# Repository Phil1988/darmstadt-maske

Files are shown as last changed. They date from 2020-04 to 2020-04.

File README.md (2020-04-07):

# Darmstadt-Maske: Gesichtsmasken für hub-rheinmain und hub-darmstadt

Warum denn "noch eine Maske"? 

Gute Frage - wir haben nach etlichen Erfahrungswerten festgestellt, dass die Prusa-Masken zwar sinnvoll sind und sich zurecht als das Maß für die Masken etabliert hat, aber einige Interessenten fragten nach einer größeren Entfernung zwischen Gesicht und Visier oder der Möglichkeit auch andere, besser desinfizierbare, Kopfbänder zu befestigen.
Außerdem wurde bei unserem Modell die Druckzeit durch Konstruktive veränderungen deutlich reduziert (bis zu 40% schneller).
Dieses Modell ist jedoch weiterhin vollständig kompatibel zur Prusa-Variante, da die Visiere/Schilder identisch sind.

Als groben Richtwert, kann man das Kopfteil in etwa 60min drucken - mit einer 0.4mm Düse.
Wer deutlich länger benötigt, sollte sich nochmal alle Informationen, die wir hier zusammentragen, anschauen oder mit uns in Kontakt treten.

## Qualität und Nachbearbeitung

Wir freuen uns über jeden der der sich uns anschließt und wir gemeinsam noch besser helfen können.
Bitte denkt daran, dass man mit der Herstellung dieser Maske eine gewisse Verantwortung hat.
Daher überprüft bitte selbst die Qualität eurer Drucke.

Hier ein Video das zeigt, welche mechanischer Belastung die Maske aushält:
[Youtube-Video](https://youtu.be/hdetuEkw_Qs )

Das sollte das Modell, dass ihr uns abgebt, auch schaffen.
Masken die schnell kaputt gehen, helfen den Hilfskräften nicht.
Auch täuscht das über unseren wirklich verwendbaren Lagerbestand hinweg.

Druckt das Modell mit mindestens 1mm Wandstärke (also für 0,4mm Düsen mit mindestens 3 Wänden).
Nehmt 30% Füllung/Infill als Gitternetz/Grid oder Gyroid.

Brim (und Pad) sollte auch entfernt worden sein, falls man damit druckt.
Falls man gestapelte (stack) Modelle druckt, sollten diese getrennt abgegeben werden.
Die Innenseite des Kopfteils (welche die Stirn berührt) und die Vorderseite (an die die Folie dran kommt) sollten glatt sein.

Das Druckteil wird zwar beim Zusammenbau auch nochmal überprüft, aber es erspart uns und euch Zeit und schont die Umwelt, wenn alle Modelle eine gute Qualität aufweisen.

Solltet ihr Probleme haben diese Qualität zu erreichen, dann lest zuerst bitte alle Hinweise auf dieser Seite durch und fragt uns danach um Hilfe für die passenden Druckeinstellungen.

## Modelle und ihre Bedeutung

In diesem Repository findet man im Ordner stl das aktuelle Modell.
Hier eine kleine Übersicht.
Sollten dort in Zukunft mehr Versionen dazukommen, wird diese Übersicht ergänzt.

Falls ihr Probleme mit dem Modell habt (0.8mm Nozzle) dann schreibt @Phil (slack) am besten direkt an oder öffnet hier ein Ticket/Issue.

### stl/Darmstadt_Maske_v2_ohne_pad.stl
Das aktuelle Modell. 

### stl/Darmstadt_Maske_v2_mit_pad.stl
Im Vergleich zum Modell "ohne Pad" ist hier an den Enden des Kopfbügels rechts und links ein kleines "Pad" dazugekommen.
Auf dem folgenden Bild grün markiert:

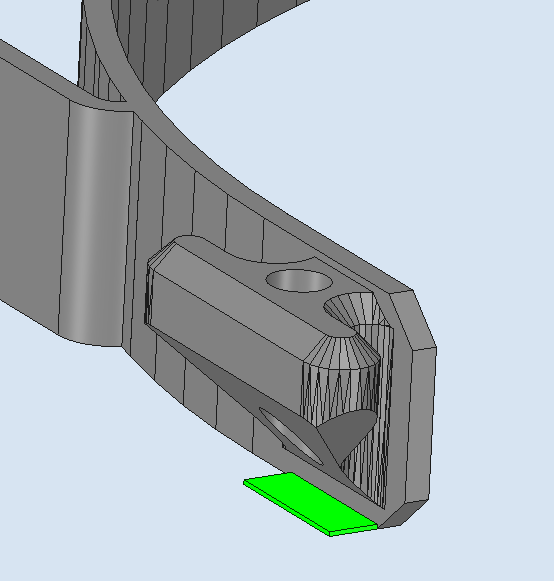
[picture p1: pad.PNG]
Veranschaulichung Pad


Das Pad erhöht an diesen Stellen die Haftung und ist für Leute zu empfehlen, die dort Probleme haben.
Es lässt sich nach dem Druck einfach mit einem Seitenschneider entfernen und liegt auf der Außenseite, damit die beim Abschnitt entstehenden scharfen Kanten nicht unangenehm an der Stirn sind.

### stl/Darmstadt_Maske_v2_Xer_Stapel_mit/ohne_pad.stl
Dies sind gestapelte Modelle mit und ohne "Pad".
Durch die Stapelung, können mehrere Modelle (z.B. über Nacht) an einem Stück gedruckt werden.
Leider fällt hierdurch aber ein zusätzlicher Arbeitsschritt an, da man die Modelle an den Sollbruchstellen erst lösen muss.

## Wohin mit den gedruckten Modellen und Material?
Du kannst alles, am besten mit deinem Namen drauf, im Makerspace Darmstadt e.V. abgeben. 
Das ist unsere zentrale Sammelstelle in Darmstadt.

## Slicer-Einstellungen

* Nutzt den `PrusaSlicer` und aktiviert den Experten-Modus (rechts oben).

**Unter Druckeinstellungen -> Schichten und Umfänge (Layers and Perimeters):**
* Setzt eine `Schichthöhe` (`Layer height`) von 0.3mm und stellt die `Konturen` (`Permiters`) bei 0,4mm Düse auf 3, bei 0,8mm Düse auf 2.

**Unter Druckeinstellungen -> Infill:**
* Setzt das Infill auf auf 30% und nehmt Gitternetz/Grid oder Gyroid. Das druckt minimal langsamer als ohne Infill, ist aber stabiler.

**Unter Druckeinstellungen -> Geschwindigkeit (Speed):**
* Alle Geschwindigkeiten auf die Geschwindigkeit `Eilgang` (`Travel Speed`) stellen, außer `Stützstrukturen` (`Support Material`), `Überbrückungen` (`Bridges`) und `Druckgeschwindigkeit der ersten Schicht` (`First layer speed`). Die echte Druckgeschwindigkeit wird ohnehin durch den maximalen Material Durchsatz eures Extruders begrenzt, sodass der Drucker die eingegebenen Geschwindigkeiten nicht erreichen wird.
* Setzt die in eurem Filament die Maximale Volumengeschwindigkeit (`Max. Volumetric Speed`) auf 8mm³/s. Das könnt ihr erhöhen bis der Druck unsauber wird. Geeignet sind 2mm³/s Stufen. Sollte es zu lauten Knackgeräuschen aus dem Extruder kommen, ist der Wert zu hoch.

**Unter Druckeinstellungen -> Erweiterte Einstellungen (Advanced):**
* Die Extrusionsbreite ist abhängig von eurem Drucker. Sollten die Außenwände sich nicht richtig verbinden, ändert die Extrusionsbreite `Konturen` (`Perimeter`) und `Außenkonturen` (`External Perimeter`) auf etwas breiter. Richtwerte für 0,4mm Düsen ist 0.48mm Bahnbreite und für 0,8mm Düsen 0,87mm Bahnbreite.

## Erklärung zu den Druckeinstellungen

Wichtig ist, dass ihr beachtet, dass euer Drucker Grenzen hat, die wir nicht kennen.
Alle hier genannten Werte für die Geschwindigkeit sind Richtwerte für unsere Drucker.
Im Zweifel solltet ihr euch lieber erstmal an diese Werte ran tasten

Die Druckgeschwindigkeit wird maßgeblich von der Förderrate oder der `Maximalen Volumengeschwindigkeit` (`Max. Volumetric Speed`) beeinflusst. Das Modell ist simpel und hat ein gewisses Volumen, das durch den Druckkopf gedrückt werden muss. Ist diese Fördermenge kleiner, dauert der Druck länger. Angegeben wird diese in mm³/s. Richtwert für PLA ist etwa 10-12mm³/s.
Um die Fließeigenschaften des Kunststoffes zu verbessern, kann es ratsam sein, die Temperatur um 5-10°C höher zu stellen.

Als Schichthöhe drucken wir größtenteils mit 0,3mm.

Weiterhin möchte man Dinge vermeiden, die den Druckkopf bremsen. Dazu gehört langsam gedruckte Lückenfüllungen (`Gap fill`), Infill und andere enge Radien, bei denen der Drucker langsam fahren muss.

Als Beispiel hier ein Bild, mit dunkelrotem Infill und weißer Lückenfüllung, die beide sehr langsam gedruckt werden.
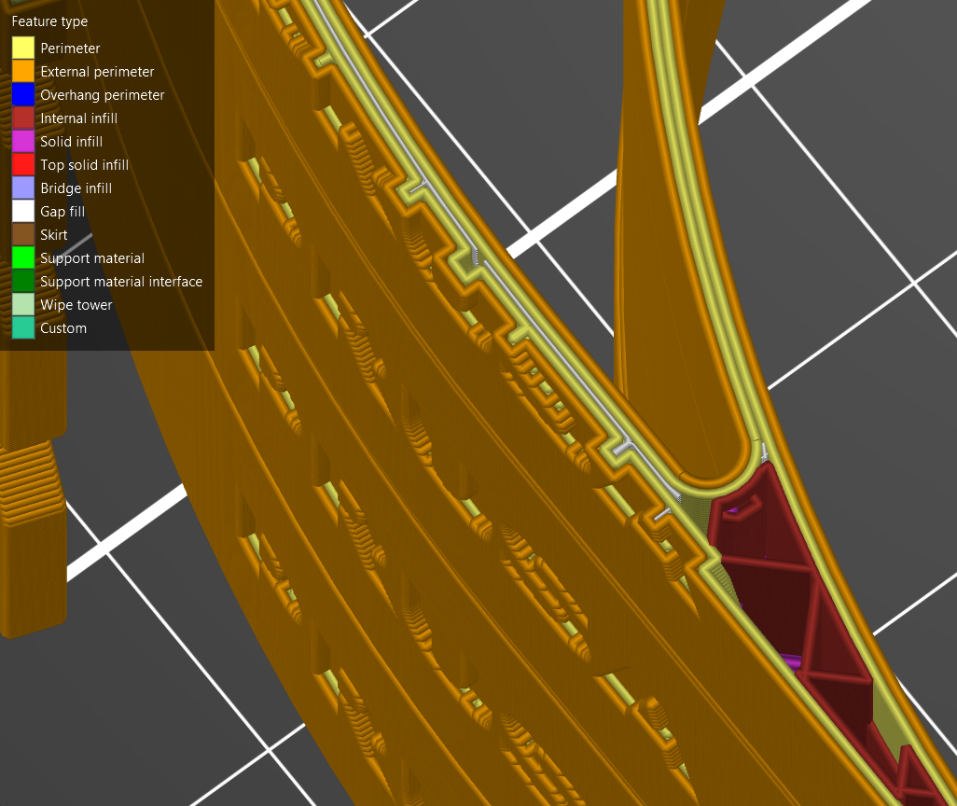
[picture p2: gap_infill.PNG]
Gap Fill and Infill


Dieses Beispiel zeigt ein Bild unseres Modells, was nur aus Bahnen, hier 4 Konturen (Perimeters), besteht und daher sehr schnell gedruckt werden kann.
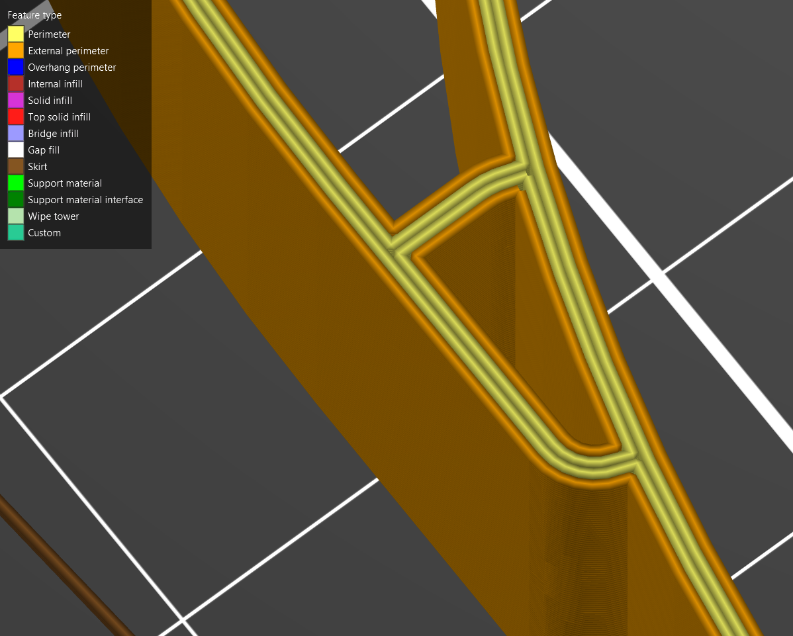
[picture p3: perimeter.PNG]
Only Perimeters


Um schnell druckbare Objekte zu bekommen, muss man in der Regel beim Design ansetzen. Bei dem Modell der Darmstadt-Maske wurde darauf geachtet, die Wandstärke von 1.67mm einzuhalten, um eine glatte Anzahl gängiger Spurbreiten zu erhalten. So kann auf die ausbremsende Lückenfüllungen verzichtet werden. Deswegen ist die Einstellung der richtigen Extrusionsbreite entscheidend. 
Für eine 0.4mm Düse, ist eine Bahnbreite von 0.48mm ein guter Startwert. Man sollte aber beim Slicen selbst die Bahnen prüfen und die Breite entsprechend anpassen.

Da letzten Endes nur die maximal mögliche Volumengeschwindigkeit relevant ist, kann der Drucker also in allen anderen Geschwindigkeiten auf seine maximale Geschwindigkeit eingestellt werden (z.B. 100mm/s). Hier eignet sich der Wert der unter `Eilgang` (`Travel Speed`) eingetragen ist. Wichtig: Sollten gestapelte Versionen gedruckt werden, so ist wichtig, dass der Haken bei `Umfangbrücken entdecken` (`Detect bridging Perimeters`) gesetzt und die Geschwindigkeit von Brücken auf einen sehr niedrigen Wert gesetzt ist. Sinnig sind hier ca. 30-50mm/s. Das erleichtert später den Prozess des Zerlegens. Die Geschwindigkeit für Lückenfüllungen sollte auf 0 gesetzt werden, um diese ganz zu vermeiden.

Anschließend kann der Gcode aus dem Modell generiert werden. Die Druckdauer sollte sich nicht nennenswert oberhalb einer Stunde pro Maske befinden. Wenn doch, bitte unten in der Rubrik Troublshooting nachschauen oder mit uns in Verbindung setzen (z.B. slack, telegram, hier ein issue eröffnen, etc.).

## FAQ

Q: Warum druckt ihr eigene Designs? Es gibt doch schon so viele!

A: Das ist richtig, wir haben uns allerdings entschieden ein etwas anderes Design als bspw. Prusa zu verwenden, um eine in unseren Augen bessere Balance zwischen Druckzeit, Stabilität und Tragekomfort zu erreichen. Weiterhin ist die darmstadt-maske vollständig kompatibel zu den bei Prusa genutzten Knopfloch-Gummi-Bändern und den Visieren. Der hervorstechendste Unterschied ist ein größerer Abstand zwischen dem Gesicht und dem Visier. Außerdem kann das Modell, durch eine für die meisten 3D Drucker besser optimiertes Design, vergleichsweise schnell gedruckt werden. Zusätzlich wurden aber auch noch seitliche Löcher und in dem Anker (für das Kopfband) Löcher gemacht, damit man auch andere (Gummi-)Bänder verwenden kann.

Q: Ist euer Design denn stabil genug?

A: Wir sind der Ansicht, dass es keine Einschränkungen hinsichtlich der Stabilität geben sollte, auch wenn die Maske mit großen, schweren Folien (z.B. 0,8mm PETG) ausgestattet wird.

Q: Ich nutze Cura. Gibt es dafür auch ein Einstellungs-Leitfaden?

A: Aktuell nicht. Sollten wir erhöhten Bedarf sehen, könnte sich das aber ändern. Der PrusaSlicer in Version 2.2 unterstützt übrigens inzwischen auch den die Drucker der Ender 3 Serie. Vielleicht ist das eine Chance einen Blick drauf zu werfen.

## Troubleshooting

Problem: Ich kann zwischen Bahnen durchgucken oder sie halten nicht aneinander.

Lösung: Wenn die Bahnen so auseinander stehen, dass man gewissermaßen von oben das Druckbett durch das Teil sehen kann, dann solltest du versuchen, ob sich das Ergebnis mit leicht breiteren Bahnen beheben lässt. Beispielsweise 0.48mm Bahnbreite oder noch etwas mehr verwenden. Wenn sich seitlich durch den Druck gucken lässt oder sich die einzelnen Schichten voneinander ablösen, dann scheinst du zu wenig Material zu verdrucken. Das kann mehrere Gründe haben, lässt sich aber vermutlich am einfachsten durch einen höheren Extrusionsmultiplikator lösen. Eventuell ist eine geringere Schichtdicke sinvoll.

[gap_infill]: gap_infill.PNG "Infill und Lückenfüllungen"

[perimeter]: perimeter.PNG "Nur Hüllen"

## Credits

Dieses Repository ist maßgeblich beinflusst von https://github.com/yschroeder/face-shield.

## Disclaimer

Diese Gesichtsmasken sind kein medizinisches Produkt, sind nicht zertifiziert und eine Herstellung und Benutzung geschieht auf eigene Gefahr. Jegliche Haftung ist ausgeschlossen.

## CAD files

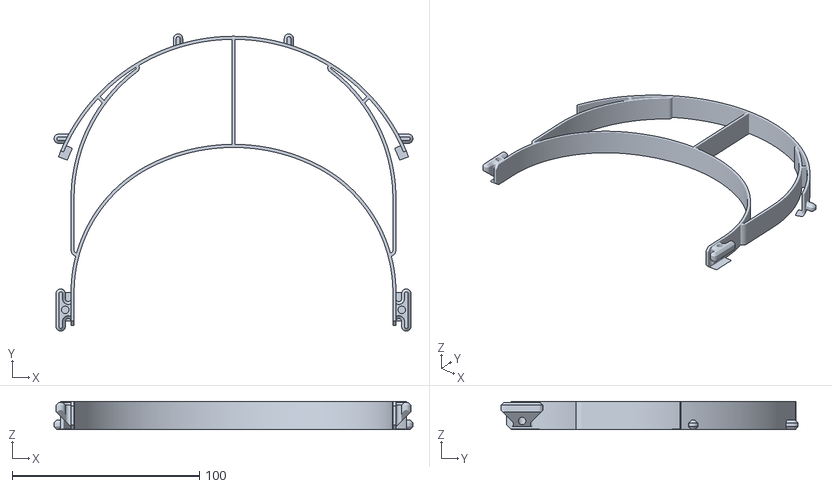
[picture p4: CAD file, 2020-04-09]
stl/V3/Darmstadt_Maske_v3_mit_pad.stl
191.5 x 158.6 x 15.0

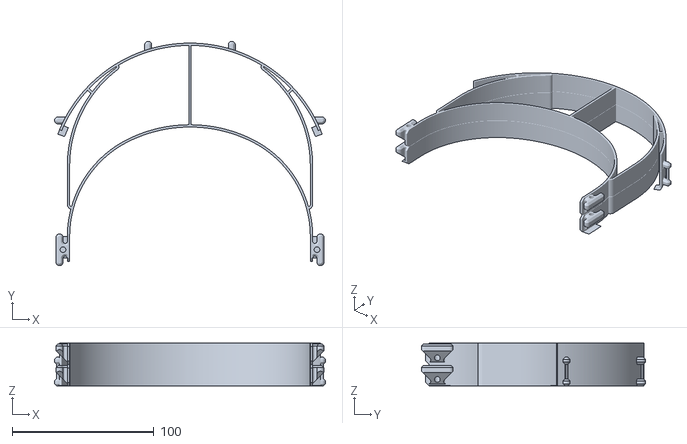
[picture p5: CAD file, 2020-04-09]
stl/V3/Stapel_0.25mm_layer/Darmstadt_Maske_v3_2er_Stapel_0.25mm_layer.stl
191.5 x 158.6 x 30.3

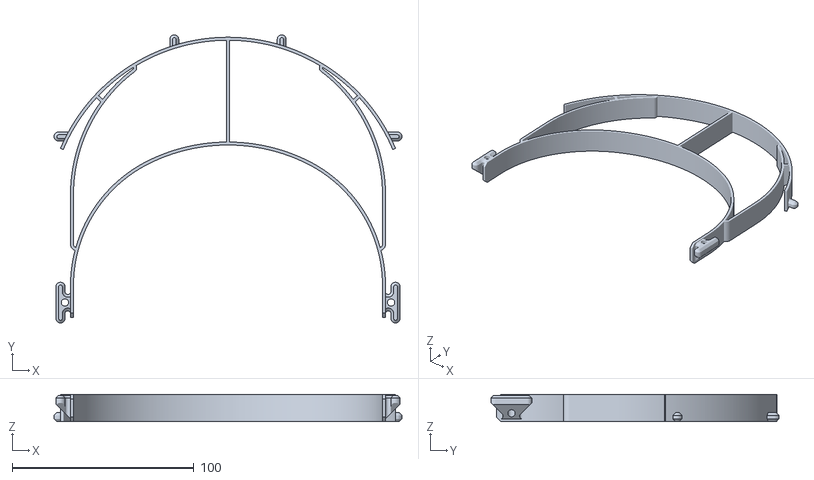
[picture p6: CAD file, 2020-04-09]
stl/V3/Darmstadt_Maske_v3_ohne_pad.stl
191.5 x 158.6 x 15.0

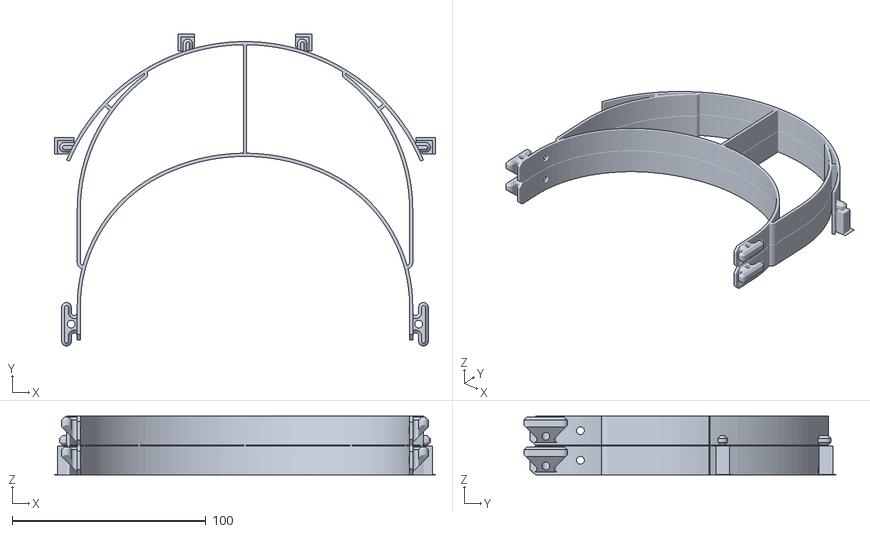
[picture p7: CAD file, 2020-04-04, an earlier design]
stl/V2 - old/Stapel_0.4mm_nozzle/Darmstadt_Maske_v2_2er_Stapel_ohne_pad.stl
196.8 x 161.2 x 30.3

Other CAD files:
stl/V3/Stapel_0.3mm_layer/Darmstadt_Maske_v3_2er_Stapel_0.3mm_layer.stl
stl/V2 - old/Darmstadt_Maske_v2_mit_pad.stl
stl/V2 - old/Darmstadt_Maske_v2_ohne_pad.stl
stl/V2 - old/Stapel_0.4mm_nozzle/Darmstadt_Maske_v2_2er_Stapel_mit_pad.stl

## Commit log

2020-04-02 Introduce STL darmstadt-maske-v1
    [darmstadt-maske-v1.stl]
2020-04-08 Readme umstrukturiert und Texte verändert (#9)
    * Update README.md
    * Add files via upload
2020-04-08 Clean up unneeded files
    [Darmstadt_Maske_v2_2er_Stapel.stl, Darmstadt_Maske_v2_2er_Stapel_mit_pad.stl, Darmstadt_Maske_v2_2er_Stapel_ohne_pad.stl, Darmstadt_Maske_v2_mit_pad.stl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]
2020-04-09 V3 mit anderen stacks in 0.3mm und 0.25mm layer heigt
    [Darmstadt_Maske_v2_2er_Stapel_mit_pad.stl, Darmstadt_Maske_v2_2er_Stapel_ohne_pad.stl, Darmstadt_Maske_v2_mit_pad.stl, Darmstadt_Maske_v2_ohne_pad.stl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]
